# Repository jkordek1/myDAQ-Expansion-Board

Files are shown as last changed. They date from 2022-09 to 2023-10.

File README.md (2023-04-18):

# myDAQ Expansion Board


[]()



 Expansion board for NI myDAQ Student Data Acquisition Device, developed in 2022 for students studying at Zagreb university of applied sciences.
 It enables quick and easy .VI development without the need of connecting different modules via breadboard and jumpers.
 
 ## Features
 - Push buttons
 - Toggle switches
 - LEDs
 - BCD decoder for seven-segment display
 - L298n H-bridge used for powering two DC motors or one stepper motor
 - ACS712ELCTR-05B-T current sense IC for motor current measurement
 - External power supply for DC motors
 - Potentiometer
 - Light dependent resistor

## Images
<p align="center">
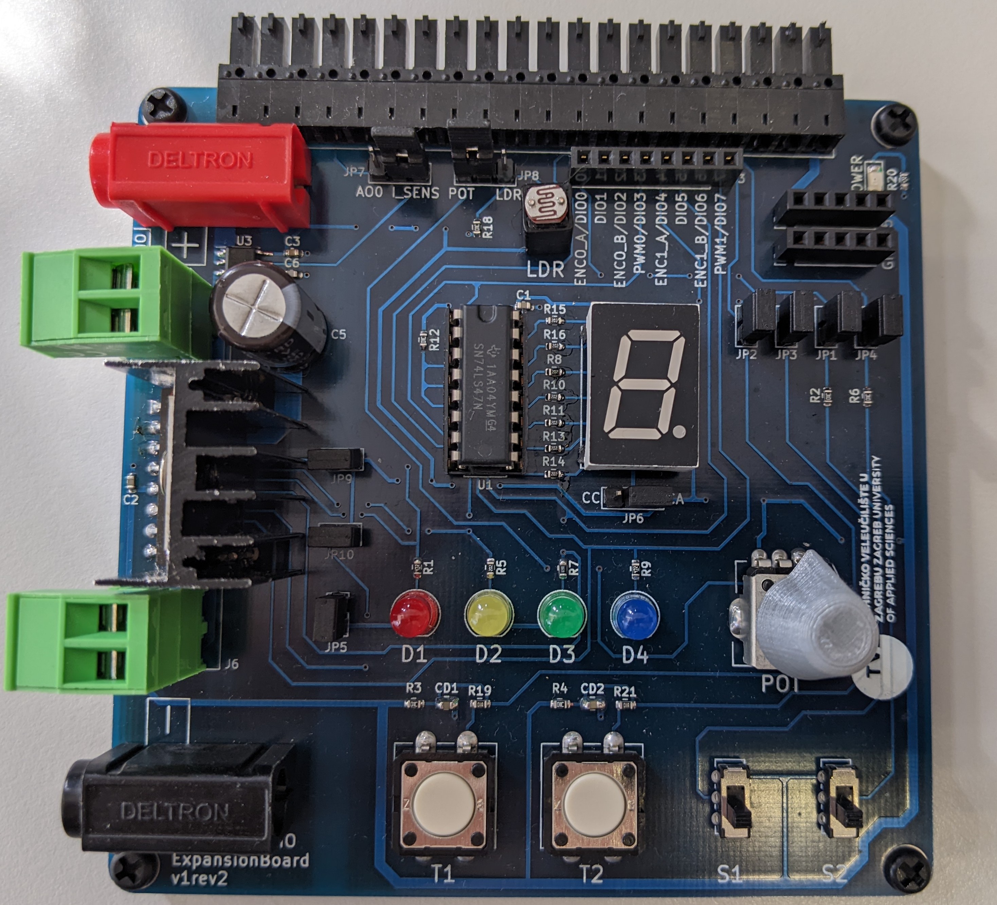
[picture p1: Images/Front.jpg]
  
</p>

## Project folder structure
    .
    ├── ...
    ├── 3DPrint                 # Files for 3D printing
    ├── Images                  # Images of the project
    ├── KiCADFiles              # Main folder
    │   ├── 3d models           # 3d models of components
    │   ├── Datasheet           # Datasheet collection
    │   ├── Graphics            # Custom graphics for PCB
    │   ├── gerber              # gerber output folder
    │   ├── myDAQExpansionBoard # Main folder for KiCAD files
    │   └── Schematic.pdf       # Project schematic
    └── ...

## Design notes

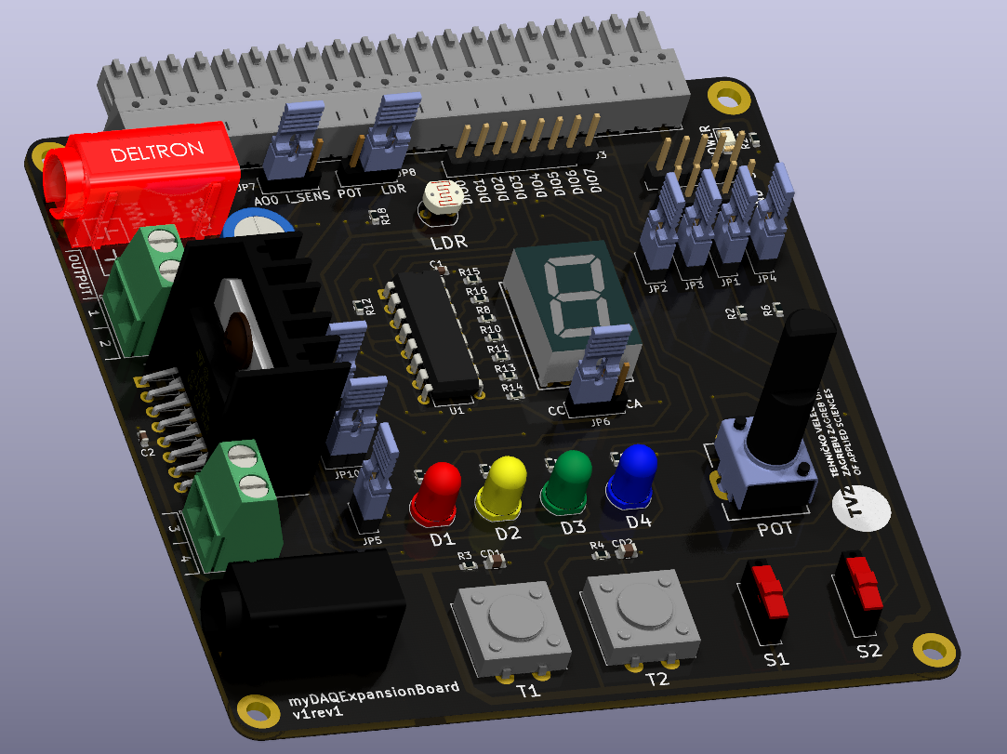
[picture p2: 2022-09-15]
Images/render_v1rev1.PNG

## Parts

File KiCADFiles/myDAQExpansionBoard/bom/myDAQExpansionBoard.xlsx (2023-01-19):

# | Naziv | Kućište | Količina | digikey/TME/mouser
1 | LED, crvena, 5mm THD | 5mm THD | 20
2 | LED, žuta, 5mm THD | 5mm THD | 20
3 | LED, zelena, 5mm THD | 5mm THD | 20
4 | LED, plava, 5mm THD | 5mm THD | 20
5 | LED, crvena, 1206 SMD | 1206 SMD | 20
6 | Otpornik 4k7, 0603 SMD | 0603 SMD | 40
7 | Otpornik 10k, 0603 SMD | 0603 SMD | 120
8 | Kondenzator 470uF, 35V | C_Radial_D10.0mm_H16.0mm_P5.00mm | 20 | 399-6657-1-ND (https://www.digikey.com/en/products/detail/kemet/ESK477M035AH2EA/3083072)
9 | Otpornik 2k, 0603 SMD | 0603 SMD | 160
10 | jumper, crni, 09200-71-BDGB00 | 09200-71-BDGB00 | 200 | 1849-09200-71-BDGB00-ND (https://www.digikey.com/en/products/detail/metz-connect-usa-inc/09200-71-bdgb00/13536314)
11 | jumper, crni, kraći, STC02SYAN | STC02SYAN | 200 | S9000-ND (https://www.digikey.com/en/products/detail/sullins-connector-solutions/STC02SYAN/76372?s=N4IgTCBcDaIMoE4AMKC0A5AIiAugXyA)
12 | Kondenzator 1uF, X7R, 50V, 0805 SMD | 0805 SMD | 40
13 | Kondenzator 1nF, X7R, 50V, 0603 SMD | 0603 SMD | 20
14 | Kondenzator 100nF, X7R, 50V, 0603 SMD | 0603 SMD | 80
15 | Potenciometar 10k, PTV09A-4225F-B103 | PTV09A-4225F-B103 | 20 | PTV09A-4225F-B103-ND (https://www.digikey.com/en/products/detail/bourns-inc/PTV09A-4225F-B103/3781155)
16 | Otpornik 619R, 0603 SMD | 0603 SMD | 20
17 | Otpornik 1k, 0603 SMD | 0603 SMD | 40
19 | 74LS47 | DIP-16_W7.62mm | 20 | TME (https://www.tme.eu/hr/details/74ls47/dekoderi-multiplekseri-prekidaci/texas-instruments/sn74ls47n/)
20 | Podnožje profi, DIP-16_W7.62mm | DIP-16_W7.62mm | 20
21 | ACS712ELCTR-05B | SOIC-8_3.9x4.9mm_P1.27mm | 20
22 | Buksna 4mm crvena PCB Deltron 571-0500 |  | 20 | 164-6219 (https://hr.mouser.com/ProductDetail/Deltron/571-0500?qs=E2gf03EXmtqN5S6PKlh9vA%3D%3D)
23 | Buksna 4mm cna PCB Deltron 571-0100 |  | 20 | 164-6218 (https://hr.mouser.com/ProductDetail/Deltron/571-0100?qs=E2gf03EXmtoqC8%2FBhoPdrg%3D%3D)
24 | Otpornik 6k8 | 0603 SMD | 20
26 | B3F-4000 |  | 40 | SW411-ND (https://www.digikey.com/en/products/detail/omron-electronics-inc-emc-div/b3f-4000/63961)
27 | Letvica, M, 2.54mm pitch, 1x20 |  | 20
28 | Letvica, Ž, 2.54mm pitch, 1x8 |  | 20
29 | Letvica, Ž, 2.54mm pitch, 1x5 |  | 20
30 | 7 segm displej, crveni, CA | 17.5x12.6mm, Terminal pitch 2.54mm, Row pitch 15.24mm | 20
31 | Ispitni kabelić, crveni, 0.8-1.0m, 5A |  | 20
32 | Ispitni kabelić, crni, 0.8-1.0m, 5A |  | 20
39 | plastična m3 matica |  |  |  | kupljeno
35 | hladnjak |  | 1
36 | Plastični odstojnik M3, duljina 5mm |  | 4
40 | gumene nožice
41 | m3 vijci i matice
42 | vijci bez glave za spojnicu
43 | enkoderi 360 impulsa
44 | navoji za 3d print

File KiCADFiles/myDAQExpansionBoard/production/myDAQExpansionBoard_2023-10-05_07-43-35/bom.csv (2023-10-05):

Designator | Footprint | Quantity | Value | LCSC Part #
C1, C2, C3, C4 | 0603 | 4 | 100n
C5 | C_Radial_D10.0mm_H16.0mm_P5.00mm | 1 | 470u
C6 | 0603 | 1 | 1n
CD1, CD2 | 0805 | 2 | 100n
D1 | LED_D5.0mm | 1 | RED
D10, D11, D12, D5, D6, D7, D8, D9 | D_SMA | 8 | 1N4007
D14 | 1206 | 1 | LED
D2 | LED_D5.0mm | 1 | YELLOW
D3 | LED_D5.0mm | 1 | GREEN
D4 | LED_D5.0mm | 1 | BLUE
H1, H2, H3, H4 | MountingHole_3.2mm_M3_ISO7380_Pad | 4 | MountingHole_Pad
J1, J2 | PinHeader_1x05_P2.54mm_Vertical | 2 | Conn_01x05_Male
J3 | PinHeader_1x08_P2.54mm_Vertical | 1 | Conn_01x08_Male
J4 | OSTV7XX3151 | 1 | OSTV7XX3151
J5, J6 | TerminalBlock_Phoenix_MKDS-1,5-2-5.08_1x02_P5.08mm_Horizontal | 2 | Screw_Terminal_01x02
J7 | DELTRON 4mm banana socket - red | 1 | Screw_Terminal_01x01
J8 | DELTRON 4mm banana socket - black | 1 | Screw_Terminal_01x01
JP1, JP10, JP2, JP3, JP4, JP5, JP9 | PinHeader_1x02_P2.54mm_jumper | 7 | Jumper_2_Open
JP6, JP7, JP8 | PinHeader_1x03_P2.54mm_Vertical_jumper | 3 | Jumper_3_Open
R1, R20, R9 | 0603 | 3 | 4k7
R10, R11, R13, R14, R15, R16, R5, R8 | 0603 | 8 | 2k
R12, R18, R2, R3, R4, R6 | 0603 | 6 | 10k
R17 | R_LDR_5.1x4.3mm_P3.4mm_Vertical | 1 | R_Photo
R19, R21 | 0603 | 2 | 100
R7 | 0603 | 1 | 619
RV1 | PTV09A-4225F-B502 | 1 | 10k
SW1, SW2 | EG1271A | 2 | SW_SPDT
SW3, SW4 | Omron_B3F-12x12mm | 2 | SW_Push
U1 | DIP-16_W7.62mm | 1 | 74LS47
U2 | 7segm-SA52 | 1 | 7segm-symbol
U3 | SOIC-8_3.9x4.9mm_P1.27mm | 1 | ACS712xLCTR-05B
U4 | L298n | 1 | L298N

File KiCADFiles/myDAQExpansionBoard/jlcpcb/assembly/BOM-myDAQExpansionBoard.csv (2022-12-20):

Comment | Designator | Footprint | LCSC
2k | R11 | R_0603_1608Metric
MountingHole_Pad | H1 | MountingHole_3.2mm_M3_ISO7380_Pad
BLUE | D4 | LED_D5.0mm
SW_SPDT | SW1 | 500SSP1S1M2QEA
1u | CD2 | C_0805_2012Metric
Jumper_2_Open | JP5 | PinHeader_1x02_P2.54mm_jumper
100n | C3 | C_0603_1608Metric
SW_Push | SW4 | Omron_B3F-12x12mm
Jumper_2_Open | JP10 | PinHeader_1x02_P2.54mm_jumper
10k | R3 | R_0603_1608Metric
Jumper_2_Open | JP1 | PinHeader_1x02_P2.54mm_jumper
Conn_01x05_Male | J2 | PinHeader_1x05_P2.54mm_Vertical
SW_SPDT | SW2 | 500SSP1S1M2QEA
Screw_Terminal_01x02 | J6 | TerminalBlock_Phoenix_MKDS-1,5-2-5.08_1x02_P5.08mm_Horizontal
100n | C4 | C_0603_1608Metric
YELLOW | D2 | LED_D5.0mm
2k | R13 | R_0603_1608Metric
2k | R8 | R_0603_1608Metric
MountingHole_Pad | H4 | MountingHole_3.2mm_M3_ISO7380_Pad
SW_Push | SW3 | Omron_B3F-12x12mm
Jumper_2_Open | JP2 | PinHeader_1x02_P2.54mm_jumper
Conn_01x05_Male | J1 | PinHeader_1x05_P2.54mm_Vertical
ACS712xLCTR-05B | U3 | SOIC-8_3.9x4.9mm_P1.27mm
Jumper_2_Open | JP9 | PinHeader_1x02_P2.54mm_jumper
74LS47 | U1 | DIP-16_W7.62mm
10k | R18 | R_0603_1608Metric
Jumper_2_Open | JP3 | PinHeader_1x02_P2.54mm_jumper
4k7 | R20 | R_0603_1608Metric
1u | CD1 | C_0805_2012Metric
4k7 | R1 | R_0603_1608Metric
100n | C1 | C_0603_1608Metric
7segm-symbol | U2 | 7segm-SA52
MountingHole_Pad | H2 | MountingHole_3.2mm_M3_ISO7380_Pad
10k | R4 | R_0603_1608Metric
100n | C2 | C_0603_1608Metric
L298N | U4 | L298n
RED | D1 | LED_D5.0mm
MountingHole_Pad | H3 | MountingHole_3.2mm_M3_ISO7380_Pad
Screw_Terminal_01x01 | J8 | DELTRON 4mm banana socket - black
2k | R14 | R_0603_1608Metric
Jumper_2_Open | JP4 | PinHeader_1x02_P2.54mm_jumper
R_Photo | R17 | R_LDR_5.1x4.3mm_P3.4mm_Vertical
2k | R15 | R_0603_1608Metric
10k | R12 | R_0603_1608Metric
2k | R10 | R_0603_1608Metric
10k | R6 | R_0603_1608Metric
2k | R16 | R_0603_1608Metric
GREEN | D3 | LED_D5.0mm
2k | R5 | R_0603_1608Metric
1k | R19 | R_0603_1608Metric
Screw_Terminal_01x02 | J5 | TerminalBlock_Phoenix_MKDS-1,5-2-5.08_1x02_P5.08mm_Horizontal
Conn_01x08_Male | J3 | PinHeader_1x08_P2.54mm_Vertical
Screw_Terminal_01x01 | J7 | DELTRON 4mm banana socket - red
6k8 | R9 | R_0603_1608Metric
619 | R7 | R_0603_1608Metric
10k | R2 | R_0603_1608Metric
OSTV7XX3151 | J4 | OSTV7XX3151
470u | C5 | C_Radial_D10.0mm_H16.0mm_P5.00mm
Jumper_3_Open | JP8 | PinHeader_1x03_P2.54mm_Vertical_jumper
10k | RV1 | PTV09A-4225F-B502
Jumper_3_Open | JP7 | PinHeader_1x03_P2.54mm_Vertical_jumper
1n | C6 | C_0603_1608Metric
Jumper_3_Open | JP6 | PinHeader_1x03_P2.54mm_Vertical_jumper
LED | D14 | LED_1206_3216Metric
1N4007 | D6 | D_SMA
1N4007 | D5 | D_SMA
1N4007 | D10 | D_SMA
1N4007 | D11 | D_SMA
1N4007 | D9 | D_SMA
1N4007 | D7 | D_SMA
1N4007 | D12 | D_SMA
1N4007 | D8 | D_SMA
1k | R21 | R_0603_1608Metric

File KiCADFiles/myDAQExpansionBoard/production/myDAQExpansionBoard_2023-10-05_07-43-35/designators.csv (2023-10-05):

C1:1
C2:1
C3:1
C4:1
C5:1
C6:1
CD1:1
CD2:1
D1:1
D10:1
D11:1
D12:1
D14:1
D2:1
D3:1
D4:1
D5:1
D6:1
D7:1
D8:1
D9:1
G***:2
H1:1
H2:1
H3:1
H4:1
J1:1
J2:1
J3:1
J4:1
J5:1
J6:1
J7:1
J8:1
JP1:1
JP10:1
JP2:1
JP3:1
JP4:1
JP5:1
JP6:1
JP7:1
JP8:1
JP9:1
R1:1
R10:1
R11:1
R12:1
R13:1
R14:1
R15:1
R16:1
R17:1
R18:1
R19:1
R2:1
R20:1
R21:1
R3:1
R4:1
R5:1
R6:1
R7:1
R8:1
R9:1
RV1:1
SW1:1
SW2:1
SW3:1
SW4:1
U1:1
U2:1
U3:1
U4:1

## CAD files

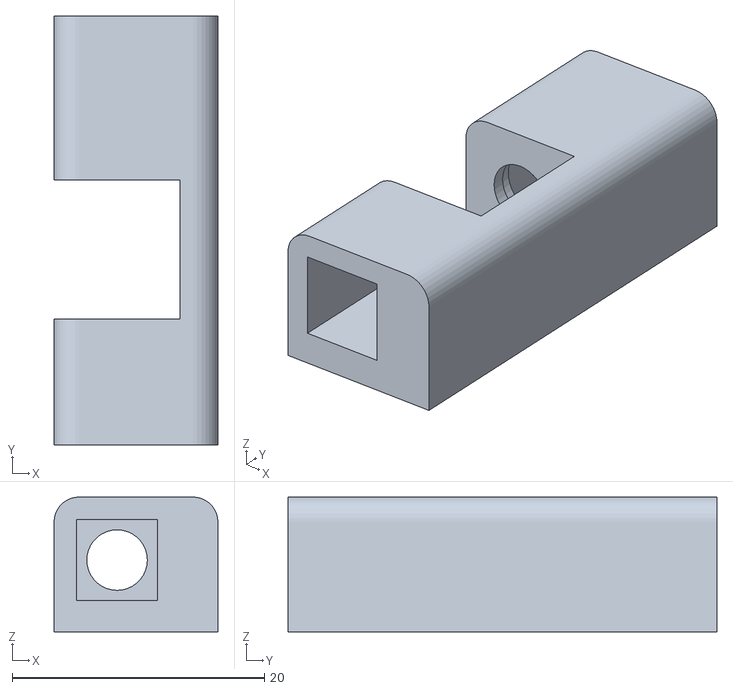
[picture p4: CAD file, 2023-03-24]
3DPrint/Drzac ledice.STL
13.0 x 34.0 x 10.7

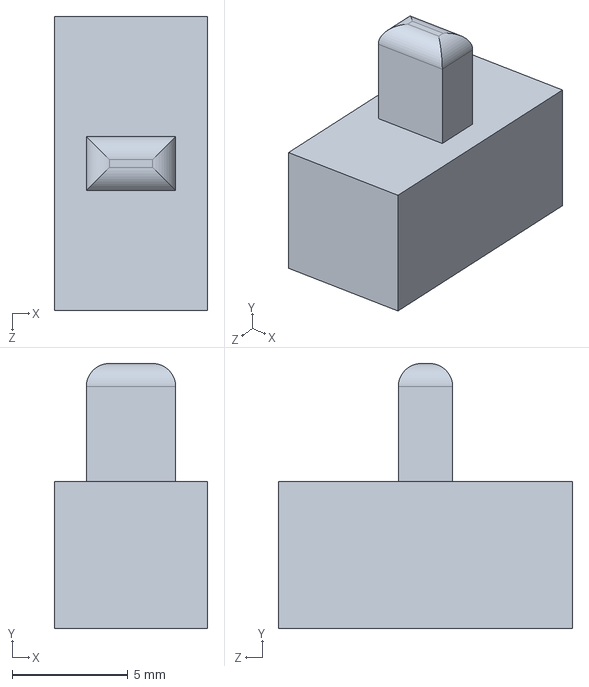
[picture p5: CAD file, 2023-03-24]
KiCADFiles/3d models/Part1.SLDPRT
6.60 x 11.4 x 12.7 mm

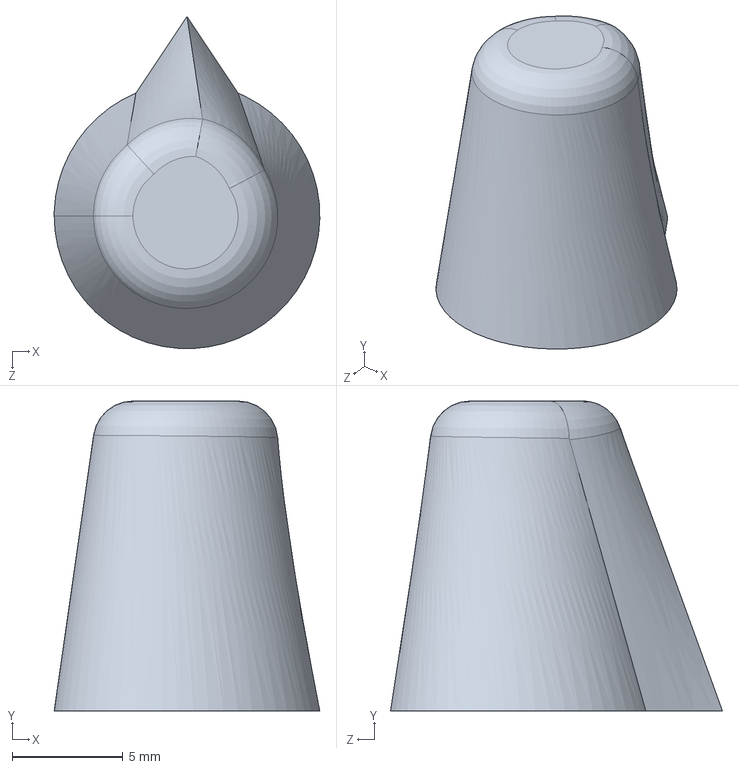
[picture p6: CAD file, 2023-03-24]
3DPrint/knob.SLDPRT
12.0 x 14.0 x 15.0 mm

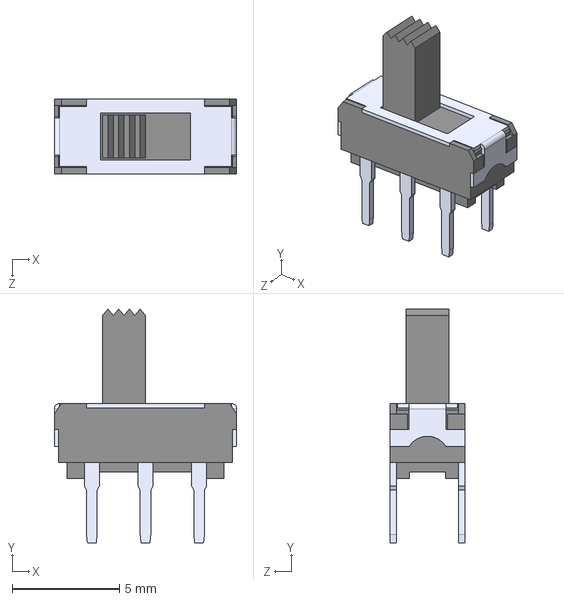
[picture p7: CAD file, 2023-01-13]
KiCADFiles/3d models/EG1271A.STEP
8.50 x 10.9 x 3.50 mm

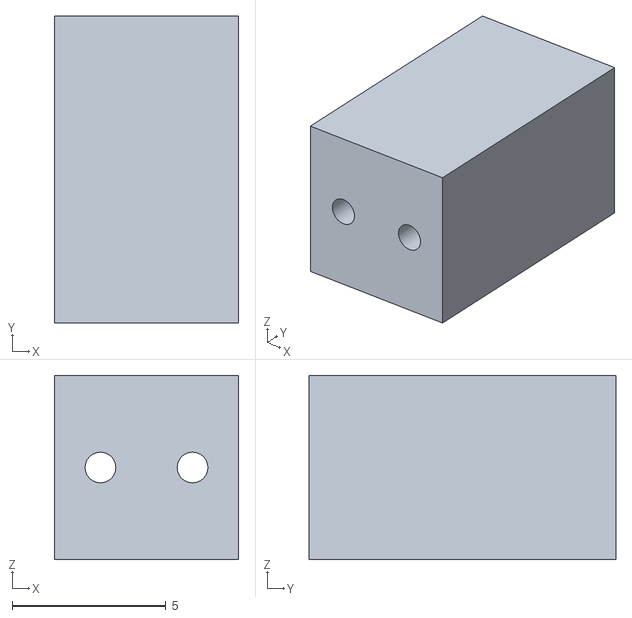
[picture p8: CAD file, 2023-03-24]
3DPrint/Odstojnik za ldr.STL
6.00 x 10.0 x 6.00

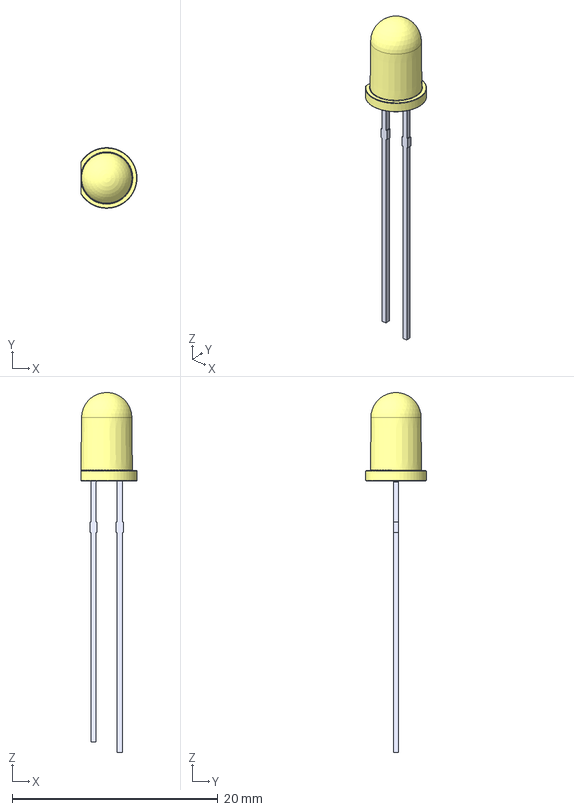
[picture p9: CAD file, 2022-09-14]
KiCADFiles/3d models/LED D5 - Yellow.step
5.45 x 5.90 x 35.0 mm

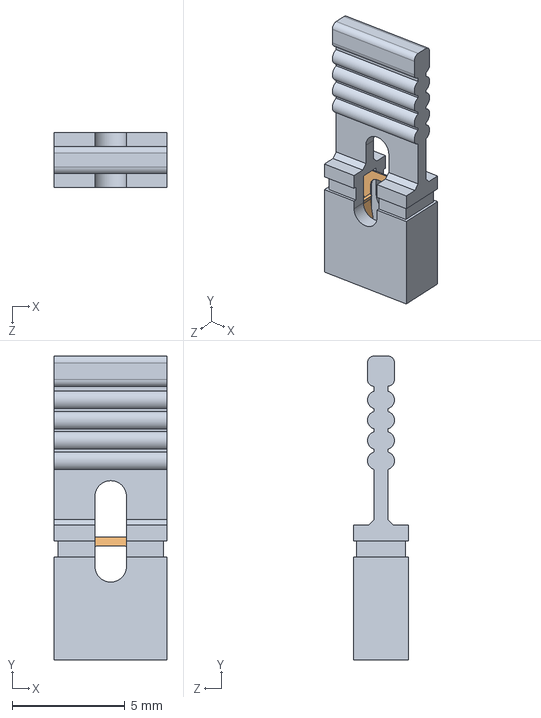
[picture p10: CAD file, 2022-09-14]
KiCADFiles/3d models/_ _C02SXON-RC.STEP
5.00 x 13.5 x 2.44 mm

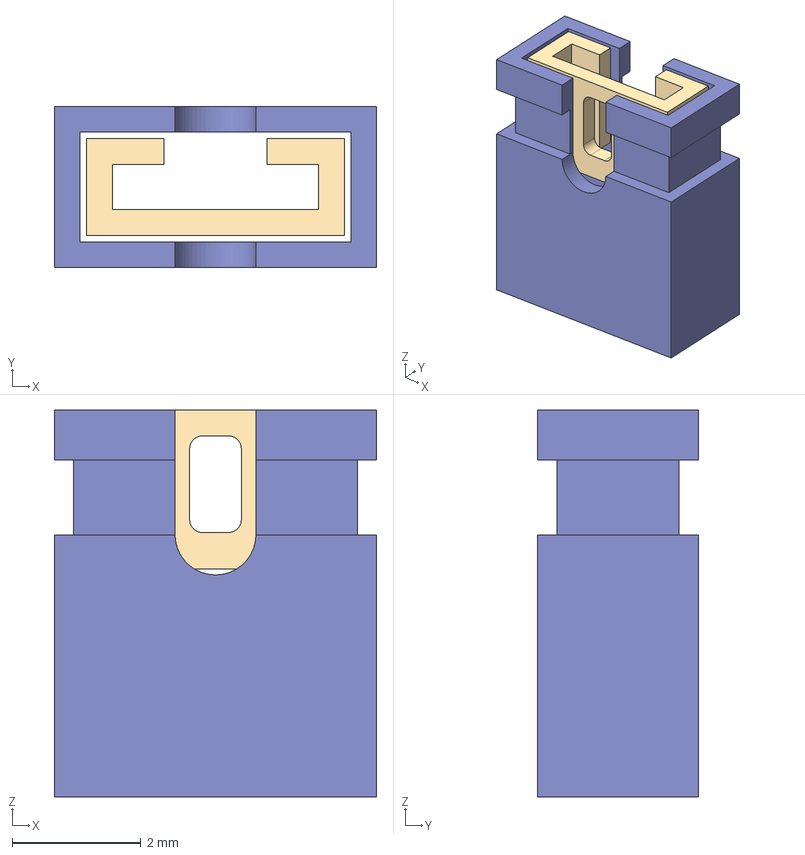
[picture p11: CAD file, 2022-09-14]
KiCADFiles/3d models/Pin header jumper.stp
5.00 x 2.50 x 6.00 mm

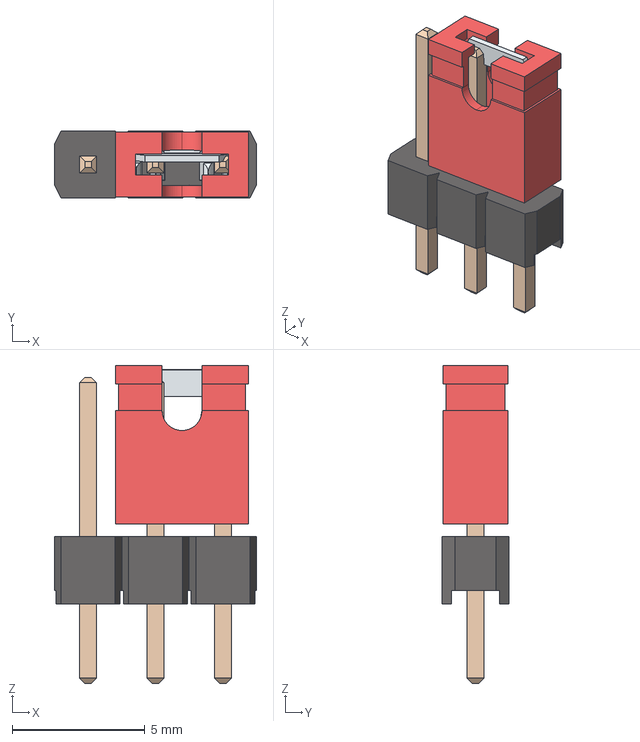
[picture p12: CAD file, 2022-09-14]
KiCADFiles/3d models/pin header 1x3 and jumper.stp
7.62 x 2.54 x 12.0 mm

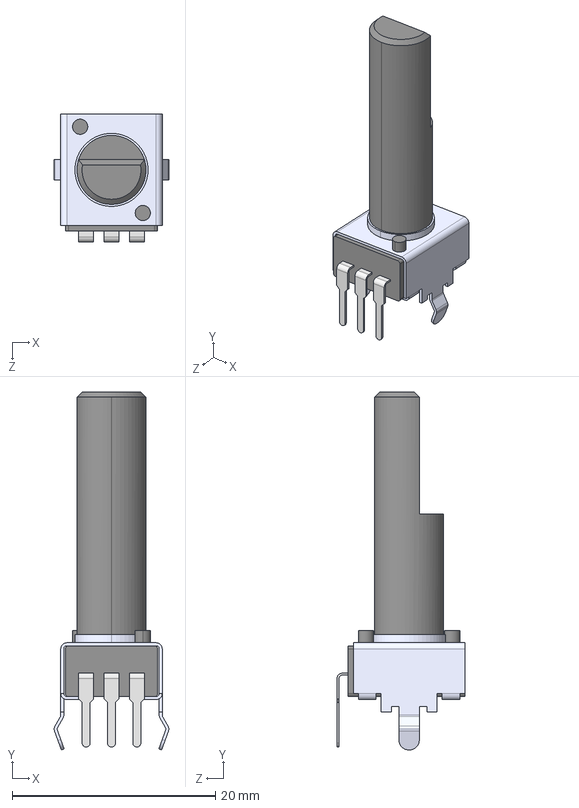
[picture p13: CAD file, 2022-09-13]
KiCADFiles/3d models/PTV09A-4.STEP
11.3 x 35.3 x 12.6 mm
櫻蠉錪1
櫻蠉錪2
櫻蠉錪3

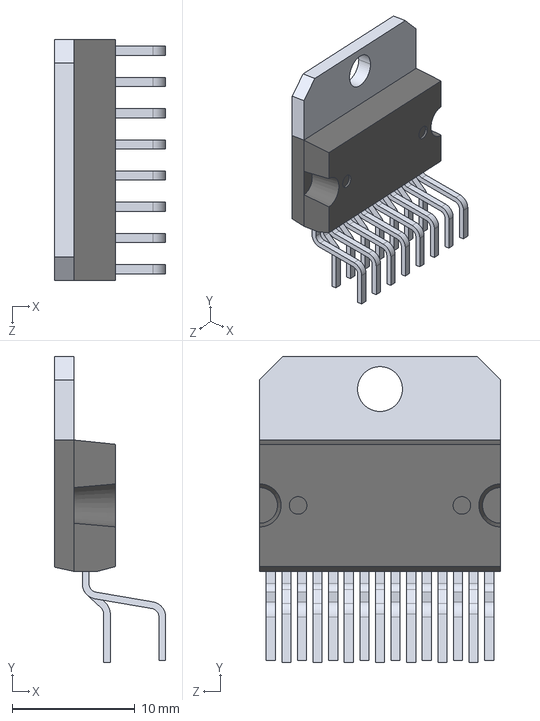
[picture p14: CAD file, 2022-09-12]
KiCADFiles/3d models/MULTIWAT T15.step
9.07 x 24.9 x 19.6 mm

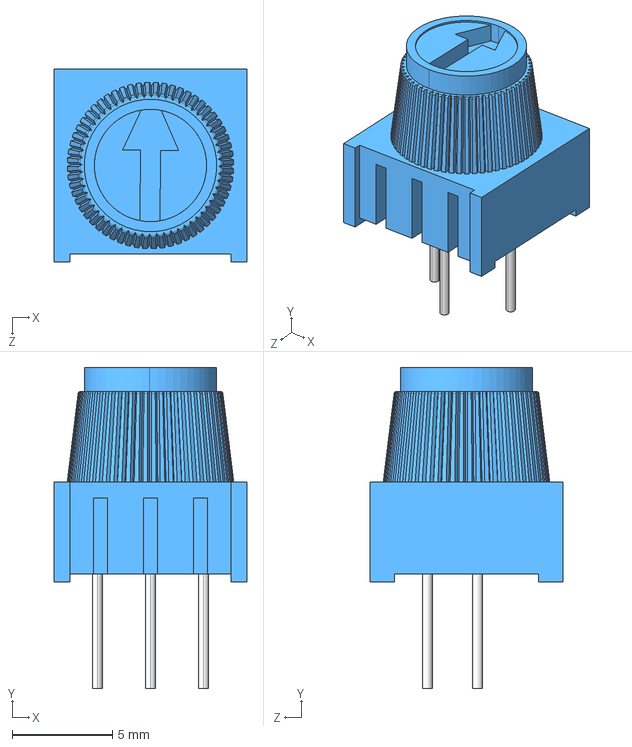
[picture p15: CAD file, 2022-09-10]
KiCADFiles/3d models/10 KILO-OHM BREADBOARD TRIM POTENTIOMETER WITH KNOB.STEP
9.60 x 16.0 x 9.60 mm
BASE, 10 KILO-OHM BREADBOARD TRIM POTENTIOMETER WITH KNOB
KNOB, 10 KILO-OHM BREADBOARD TRIM POTENTIOMETER WITH KNOB

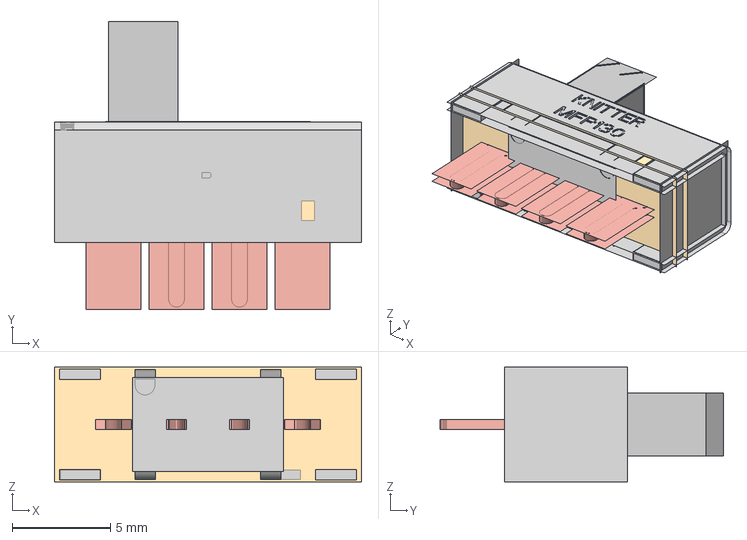
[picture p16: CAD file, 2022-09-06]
KiCADFiles/3d models/MFP 130.igs
15.6 x 14.6 x 5.82 mm

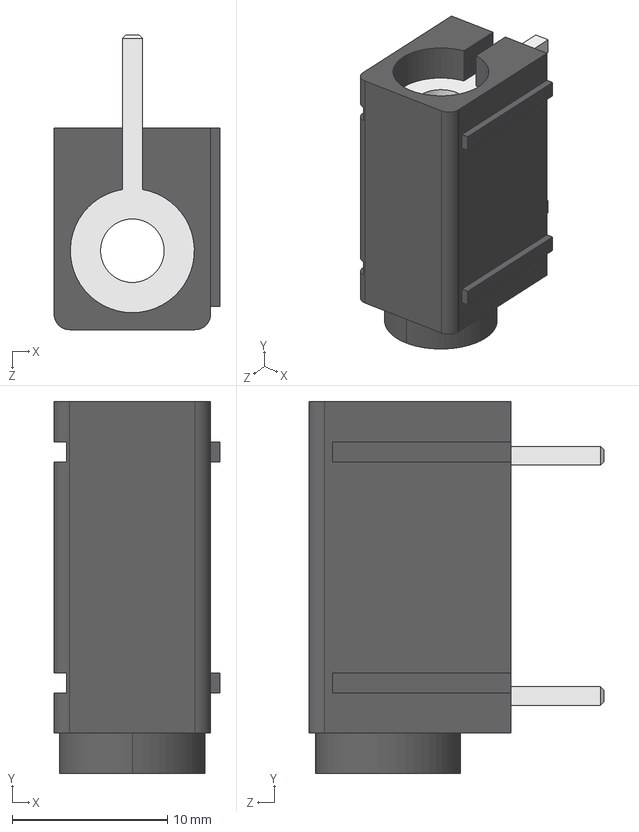
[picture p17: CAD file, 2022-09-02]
KiCADFiles/3d models/AB2_90DEG_4MM_JACK_PTH-BLK.STEP
10.7 x 24.0 x 19.0 mm

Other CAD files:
KiCADFiles/3d models/500SSP1S1M2QEA.STEP
KiCADFiles/3d models/LED D5 - Blue.step
KiCADFiles/3d models/LED D5 - Green.step
KiCADFiles/3d models/LED D5 - Red.step
KiCADFiles/3d models/B3F_4005.step
KiCADFiles/3d models/DIP-16 on SCSM-16.step
KiCADFiles/3d models/MFP_130_1682673224.214.step
KiCADFiles/3d models/OSTV7203151.stp
KiCADFiles/3d models/SX52.STEP

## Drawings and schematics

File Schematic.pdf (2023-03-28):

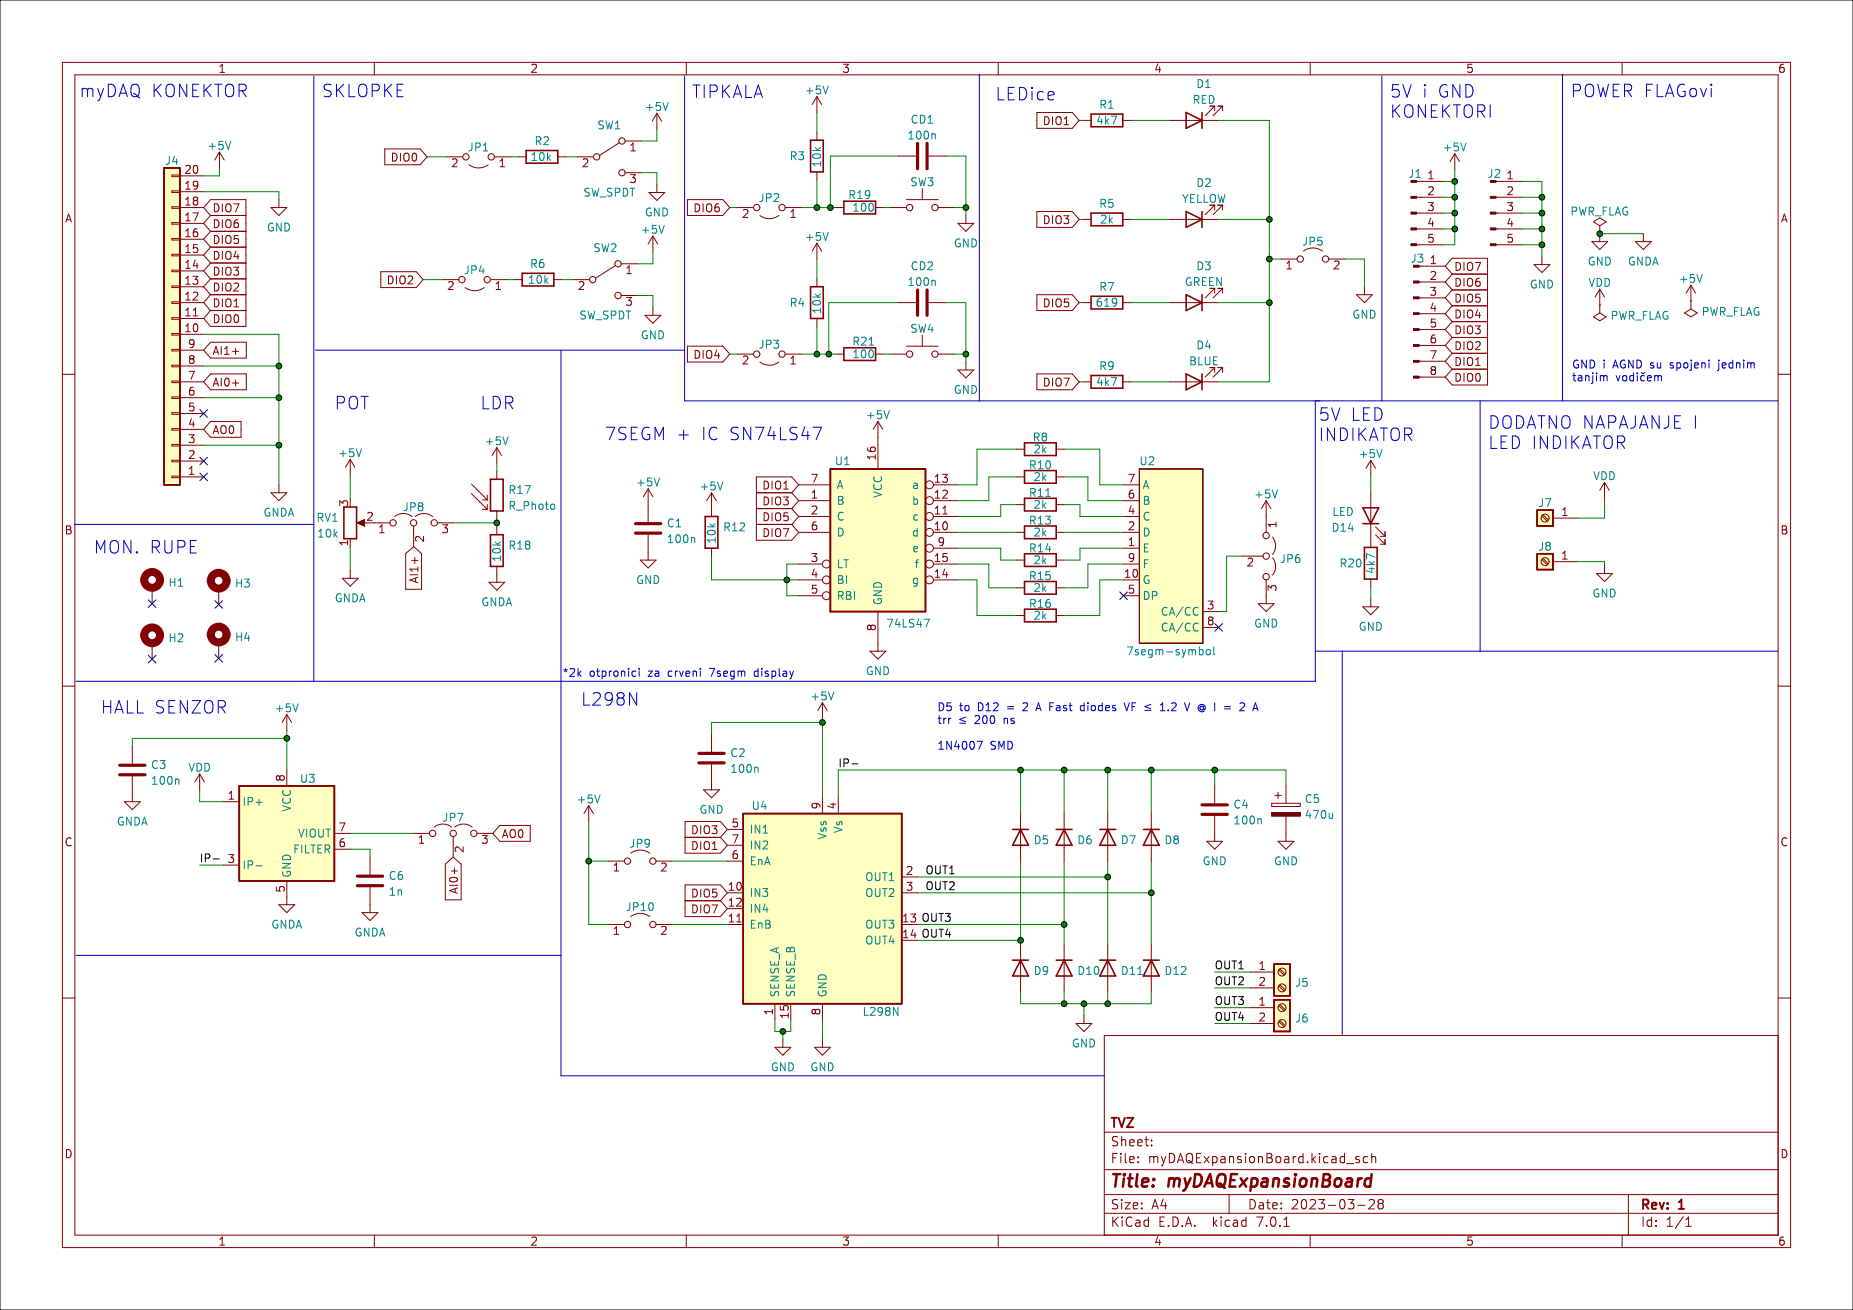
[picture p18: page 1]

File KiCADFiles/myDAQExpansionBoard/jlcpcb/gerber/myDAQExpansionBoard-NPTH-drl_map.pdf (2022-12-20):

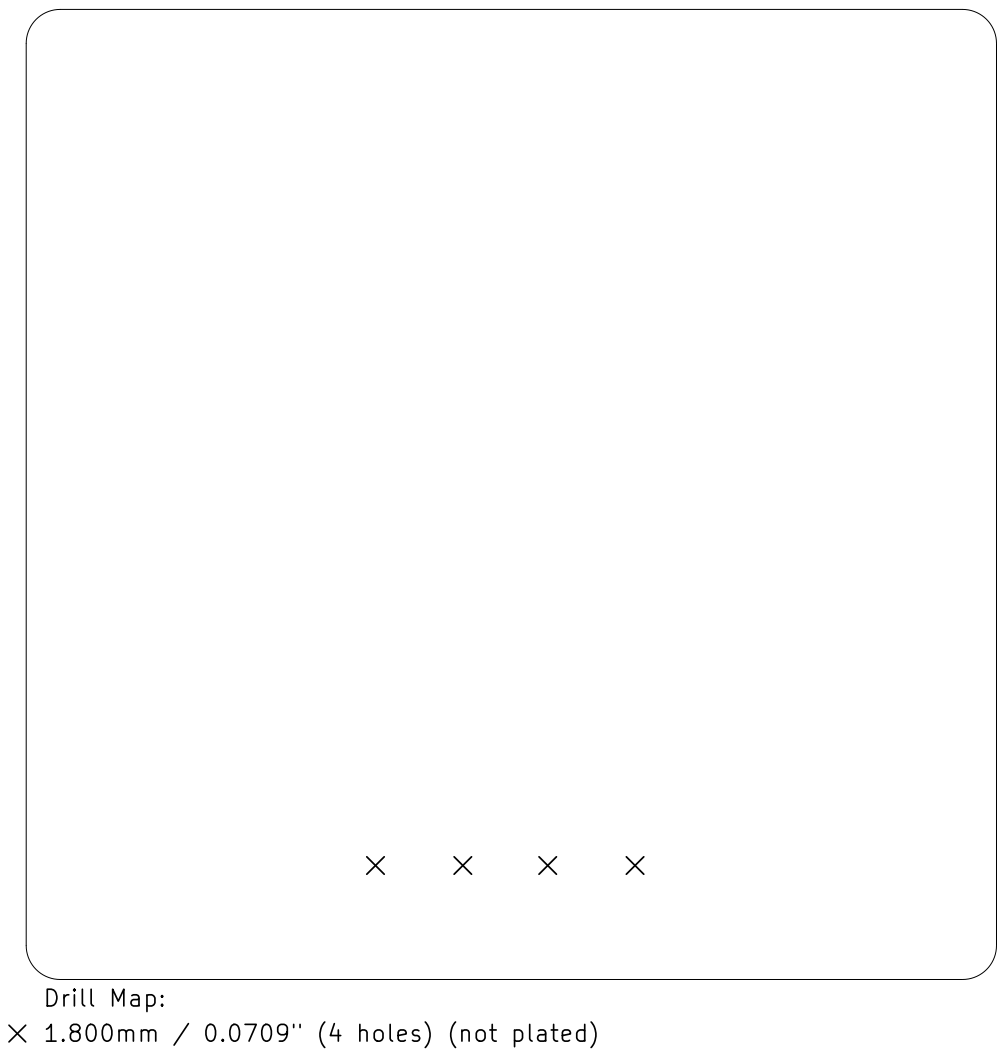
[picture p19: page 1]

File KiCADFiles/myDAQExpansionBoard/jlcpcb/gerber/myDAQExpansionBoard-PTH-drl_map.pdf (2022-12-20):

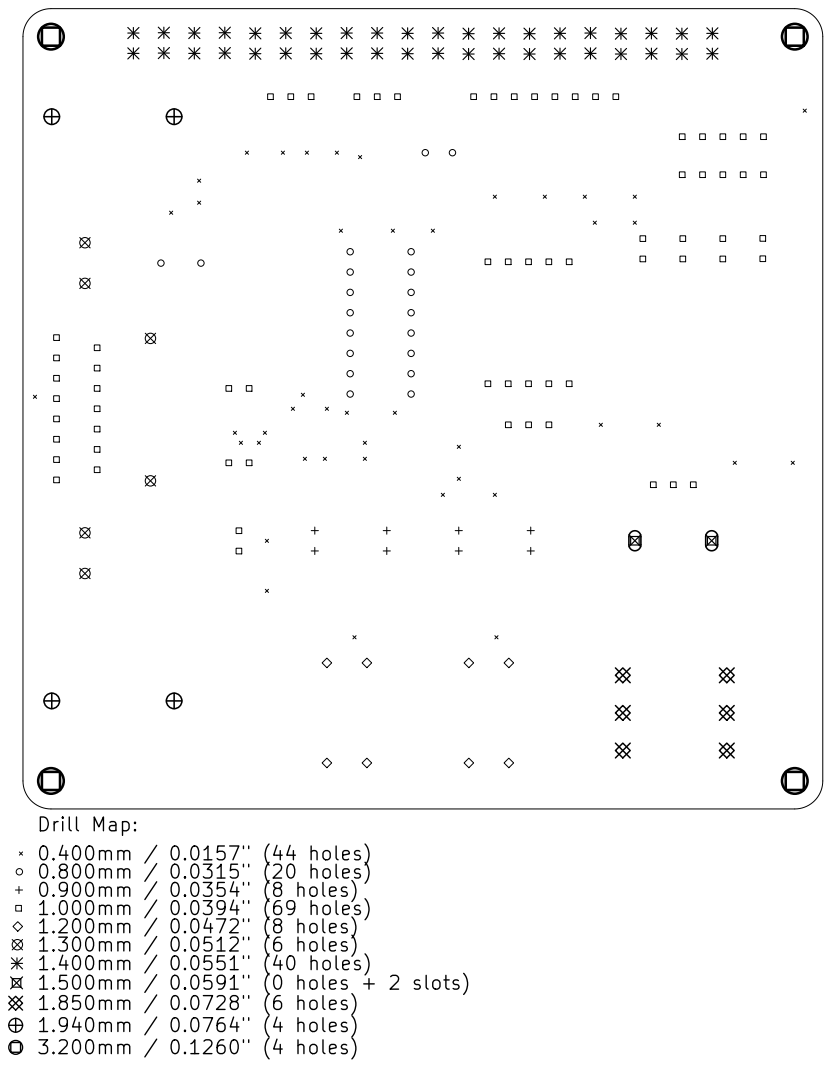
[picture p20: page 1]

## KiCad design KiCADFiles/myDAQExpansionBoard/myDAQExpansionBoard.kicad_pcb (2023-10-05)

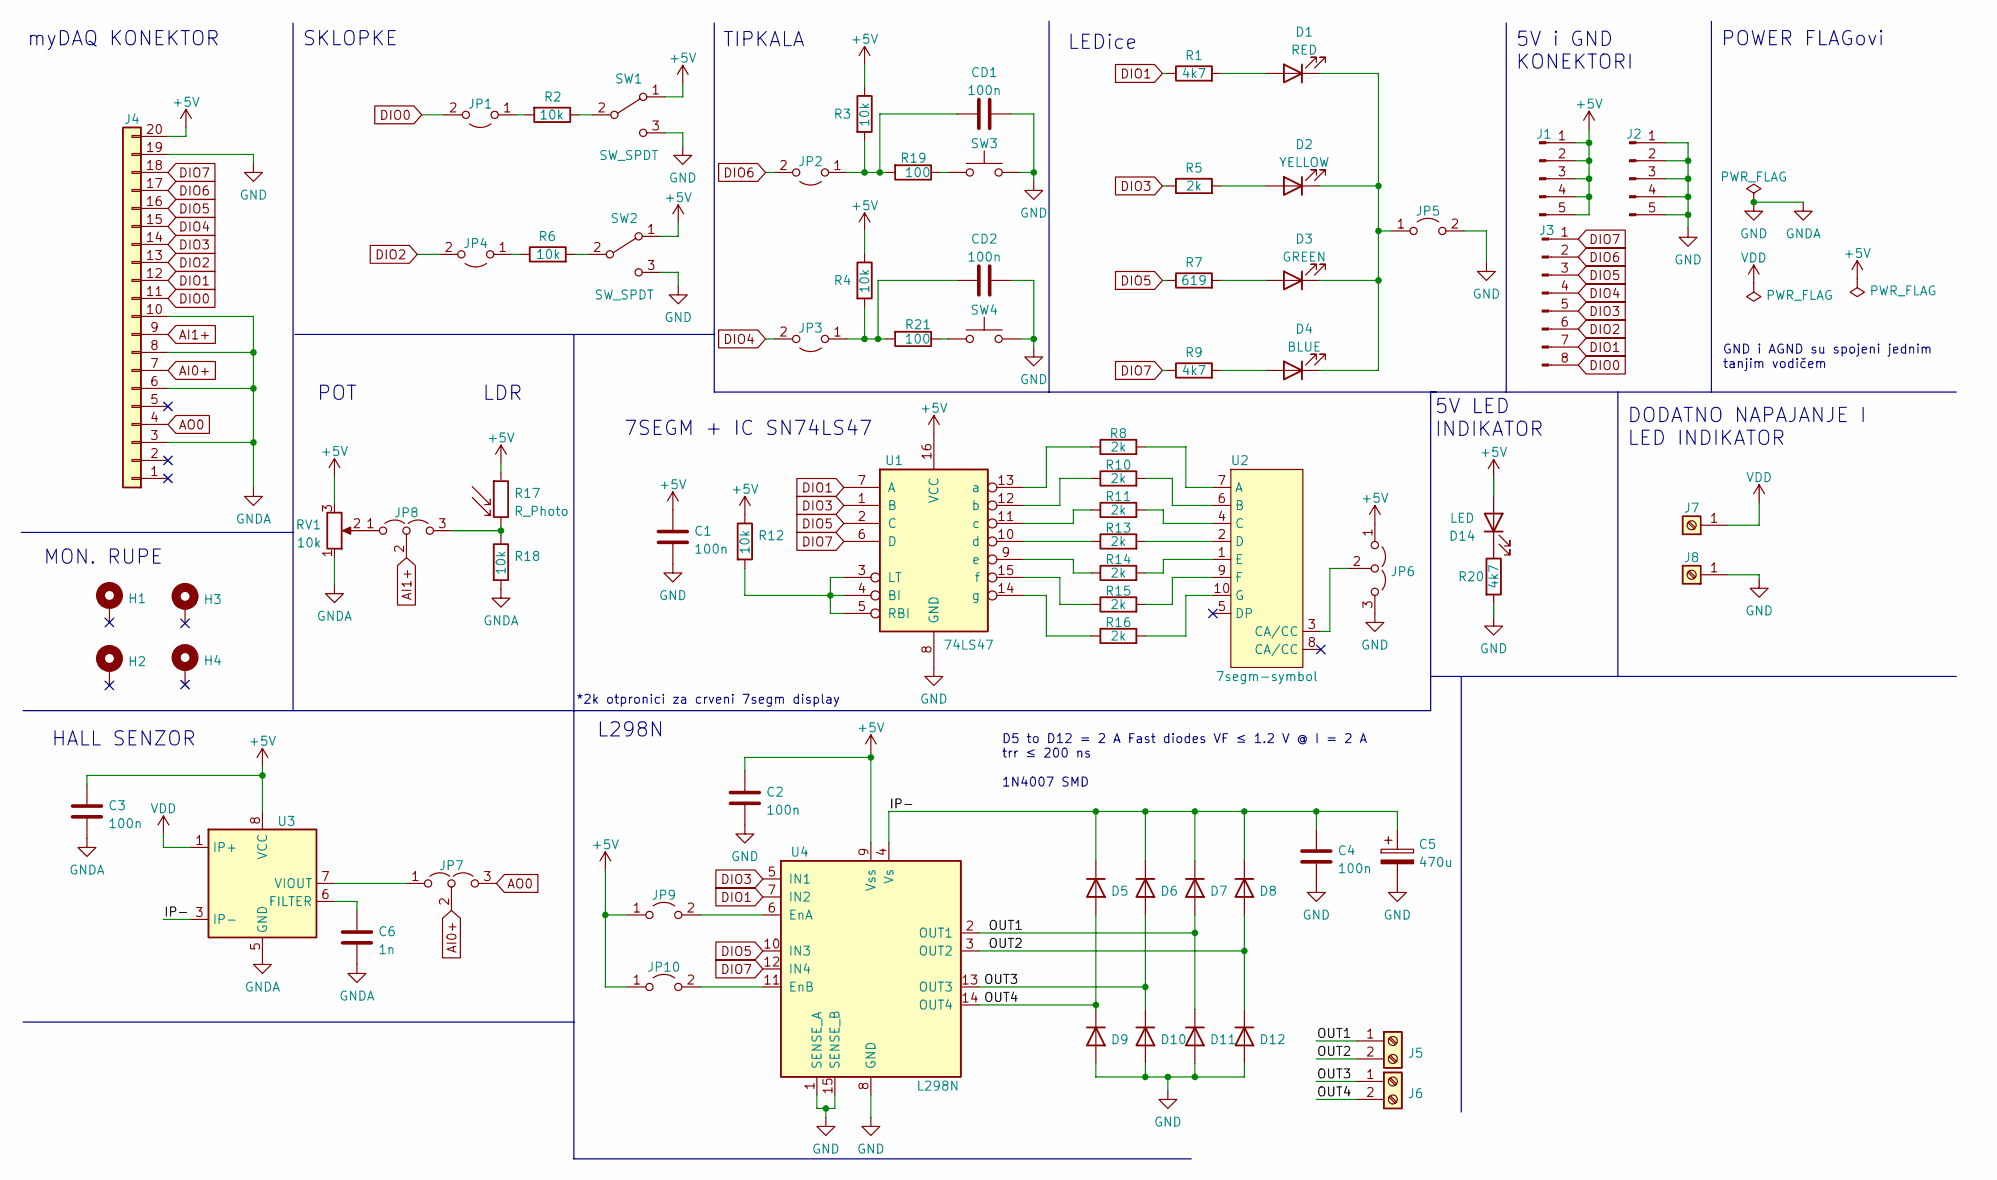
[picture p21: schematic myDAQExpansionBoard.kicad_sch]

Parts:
C1, C2, C3, C4: 100n; C_0603_1608Metric
C5: 470u; C_Radial_D10.0mm_H16.0mm_P5.00mm
C6: 1n; C_0603_1608Metric
CD1, CD2: 100n; C_0805_2012Metric
D1: RED; LED_D5.0mm
D2: YELLOW; LED_D5.0mm
D3: GREEN; LED_D5.0mm
D4: BLUE; LED_D5.0mm
D5, D6, D7, D8, D9, D10, D11, D12: 1N4007; D_SMA
D14: LED; LED_1206_3216Metric
H1, H2, H3, H4: MountingHole_Pad; MountingHole_3.2mm_M3_ISO7380_Pad
J1, J2: Conn_01x05_Male; PinHeader_1x05_P2.54mm_Vertical
J3: Conn_01x08_Male; PinHeader_1x08_P2.54mm_Vertical
J4: OSTV7XX3151
J5, J6: Screw_Terminal_01x02; TerminalBlock_Phoenix_MKDS-1,5-2-5.08_1x02_P5.08mm_Horizont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
J7: Screw_Terminal_01x01; DELTRON 4mm banana socket - red
J8: Screw_Terminal_01x01; DELTRON 4mm banana socket - black
JP1, JP2, JP3, JP4, JP5, JP9, JP10: Jumper_2_Open; PinHeader_1x02_P2.54mm_jumper
JP6, JP7, JP8: Jumper_3_Open; PinHeader_1x03_P2.54mm_Vertical_jumper
R1, R9, R20: 4k7; R_0603_1608Metric
R2, R3, R4, R6, R12, R18: 10k; R_0603_1608Metric
R5, R8, R10, R11, R13, R14, R15, R16: 2k; R_0603_1608Metric
R7: 619; R_0603_1608Metric
R17: R_Photo; R_LDR_5.1x4.3mm_P3.4mm_Vertical
R19, R21: 100; R_0603_1608Metric
RV1: 10k; PTV09A-4225F-B502
SW1, SW2: SW_SPDT; EG1271A
SW3, SW4: SW_Push; Omron_B3F-12x12mm
U1: 74LS47; DIP-16_W7.62mm
U2: 7segm-symbol; 7segm-SA52
U3: ACS712xLCTR-05B; SOIC-8_3.9x4.9mm_P1.27mm
U4: L298N; L298n

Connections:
+5V: C1.1, C2.1, C3.1, D14.2 (A), J1.1, J1.2, J1.3, J1.4, J1.5, J4.20, JP6.1 (A), JP9.1 (A), JP10.1 (A), R3.1, R4.1, R12.1, R17.1, RV1.3, SW1.1 (A), SW2.1 (A), U1.16 (VCC), U3.8 (VCC), U4.9 (Vss)
/IP-: C4.1, C5.1, D5.1 (K), D6.1 (K), D7.1 (K), D8.1 (K), U3.3 (IP-), U3.4 (IP-), U4.4 (Vs)
/OUT1: D7.2 (A), D11.1 (K), J5.1, U4.2 (OUT1)
/OUT2: D8.2 (A), D12.1 (K), J5.2, U4.3 (OUT2)
/OUT3: D6.2 (A), D10.1 (K), J6.1, U4.13 (OUT3)
/OUT4: D5.2 (A), D9.1 (K), J6.2, U4.14 (OUT4)
AI0+: J4.7, JP7.2 (C)
AI1+: J4.9, JP8.2 (C)
AO0: J4.4, JP7.3 (B)
DIO0: J3.8, J4.11, JP1.2 (B)
DIO1: J3.7, J4.12, R1.1, U1.7 (A), U4.7 (IN2)
DIO2: J3.6, J4.13, JP4.2 (B)
DIO3: J3.5, J4.14, R5.1, U1.1 (B), U4.5 (IN1)
DIO4: J3.4, J4.15, JP3.2 (B)
DIO5: J3.3, J4.16, R7.1, U1.2 (C), U4.10 (IN3)
DIO6: J3.2, J4.17, JP2.2 (B)
DIO7: J3.1, J4.18, R9.1, U1.6 (D), U4.12 (IN4)
GND: C1.2, C2.2, C3.2, C4.2, C5.2, C6.2, CD1.2, CD2.2, D9.2 (A), D10.2 (A), D11.2 (A), D12.2 (A), J2.1, J2.2, J2.3, J2.4, J2.5, J4.3, J4.6, J4.8, J4.10, J4.19, J8.1, JP5.2 (B), JP6.3 (B), R18.2, R20.2, RV1.1, SW1.3 (C), SW2.3 (C), SW3.2, SW4.2, U1.8 (GND), U3.5 (GND), U4.1 (SENSE_A), U4.8 (GND), U4.15 (SENSE_B)
unnamed: C6.1, U3.6 (FILTER)
unnamed: CD1.1, JP2.1 (A), R3.2, R19.2
unnamed: CD2.1, JP3.1 (A), R4.2, R21.2
unnamed: D1.1 (K), D2.1 (K), D3.1 (K), D4.1 (K), JP5.1 (A)
unnamed: D1.2 (A), R1.2
unnamed: D2.2 (A), R5.2
unnamed: D3.2 (A), R7.2
unnamed: D4.2 (A), R9.2
unnamed: D14.1 (K), R20.1
unnamed: JP1.1 (A), R2.2
unnamed: JP4.1 (A), R6.1
unnamed: JP6.2 (C), U2.3 (CA/CC)
unnamed: JP7.1 (A), U3.7 (VIOUT)
unnamed: JP8.1 (A), RV1.2
unnamed: JP8.3 (B), R17.2, R18.1
unnamed: JP9.2 (B), U4.6 (EnA)
unnamed: JP10.2 (B), U4.11 (EnB)
unnamed: R2.1, SW1.2 (B)
unnamed: R6.2, SW2.2 (B)
unnamed: R8.1, U1.13 (a)
unnamed: R8.2, U2.7 (A)
unnamed: R10.1, U1.12 (b)
unnamed: R10.2, U2.6 (B)
unnamed: R11.1, U1.11 (c)
unnamed: R11.2, U2.4 (C)
unnamed: R12.2, U1.3 (LT), U1.4 (BI), U1.5 (RBI)
unnamed: R13.1, U1.10 (d)
unnamed: R13.2, U2.2 (D)
unnamed: R14.1, U1.9 (e)
unnamed: R14.2, U2.1 (E)
unnamed: R15.1, U1.15 (f)
unnamed: R15.2, U2.9 (F)
unnamed: R16.1, U1.14 (g)
unnamed: R16.2, U2.10 (G)
unnamed: R19.1, SW3.1
unnamed: R21.1, SW4.1
VDD: J7.1, U3.1 (IP+), U3.2 (IP+)

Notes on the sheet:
myDAQ KONEKTOR
LEDice
5V LED INDIKATOR
*2k otpronici za crveni 7segm display
D5 to D12 = 2 A Fast diodes VF ≤ 1.2 V @ I = 2 A trr ≤ 200 ns 1N4007 SMD
5V i GND KONEKTORI
7SEGM + IC SN74LS47
POT
HALL SENZOR
POWER FLAGovi
L298N
MON. RUPE
TIPKALA
SKLOPKE
DODATNO NAPAJANJE I LED INDIKATOR
GND i AGND su spojeni jednim tanjim vodičem
LDR

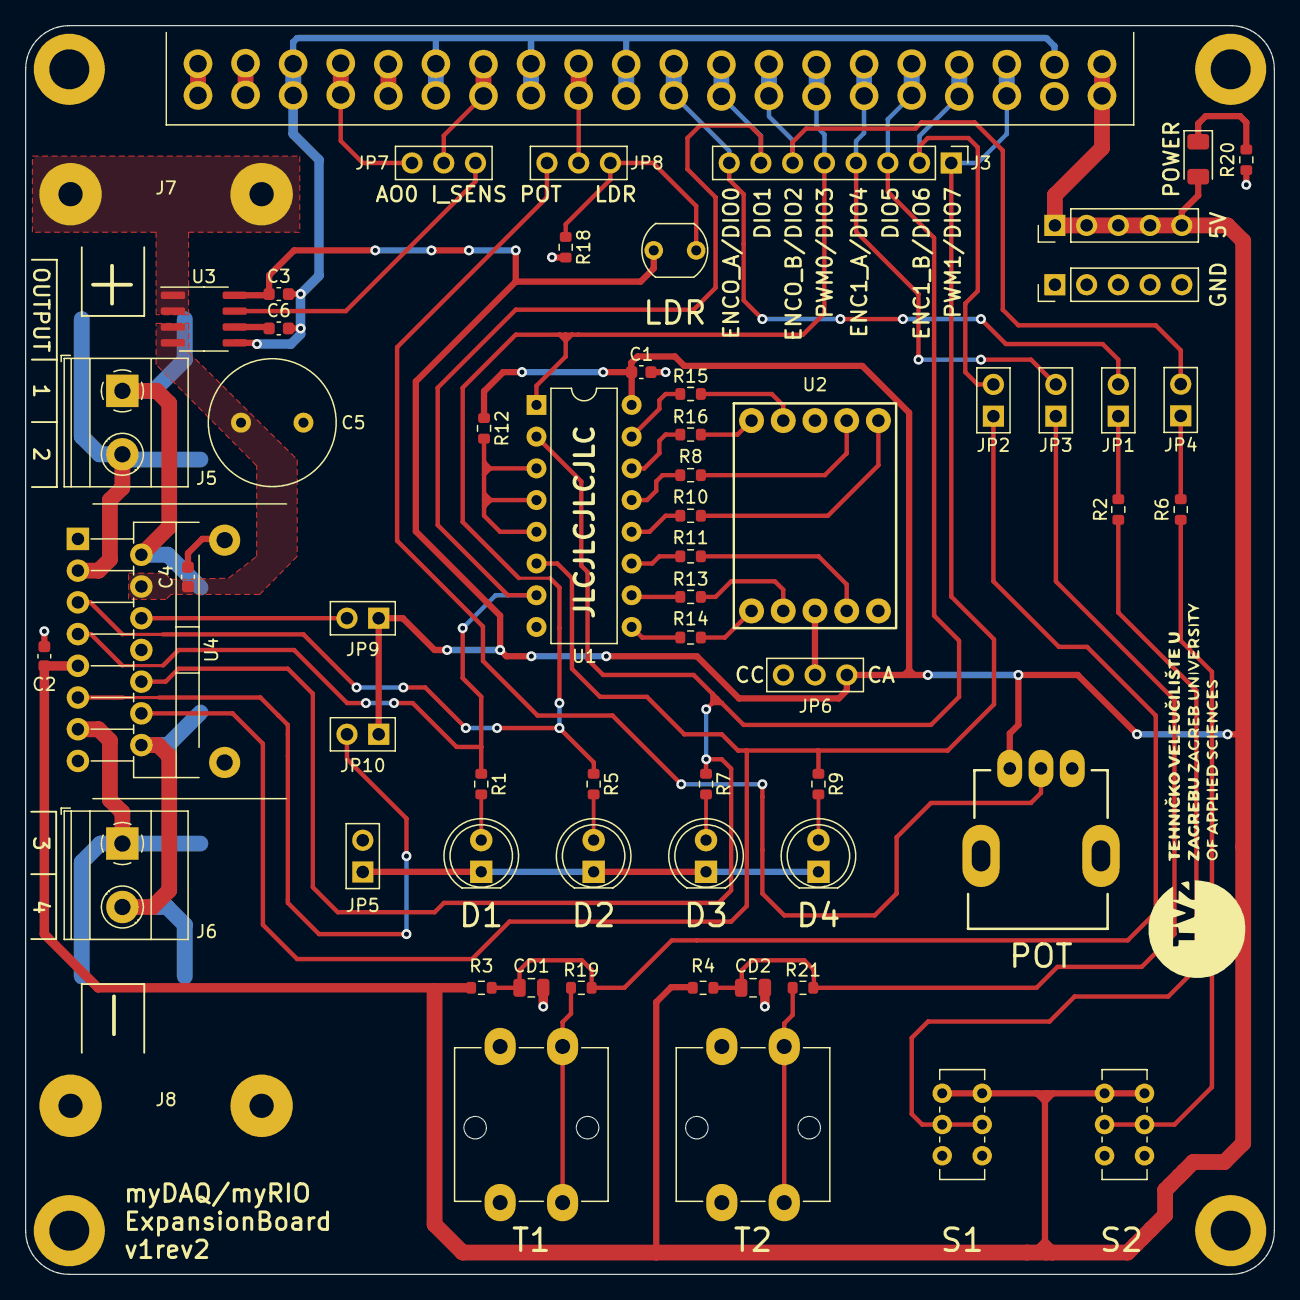
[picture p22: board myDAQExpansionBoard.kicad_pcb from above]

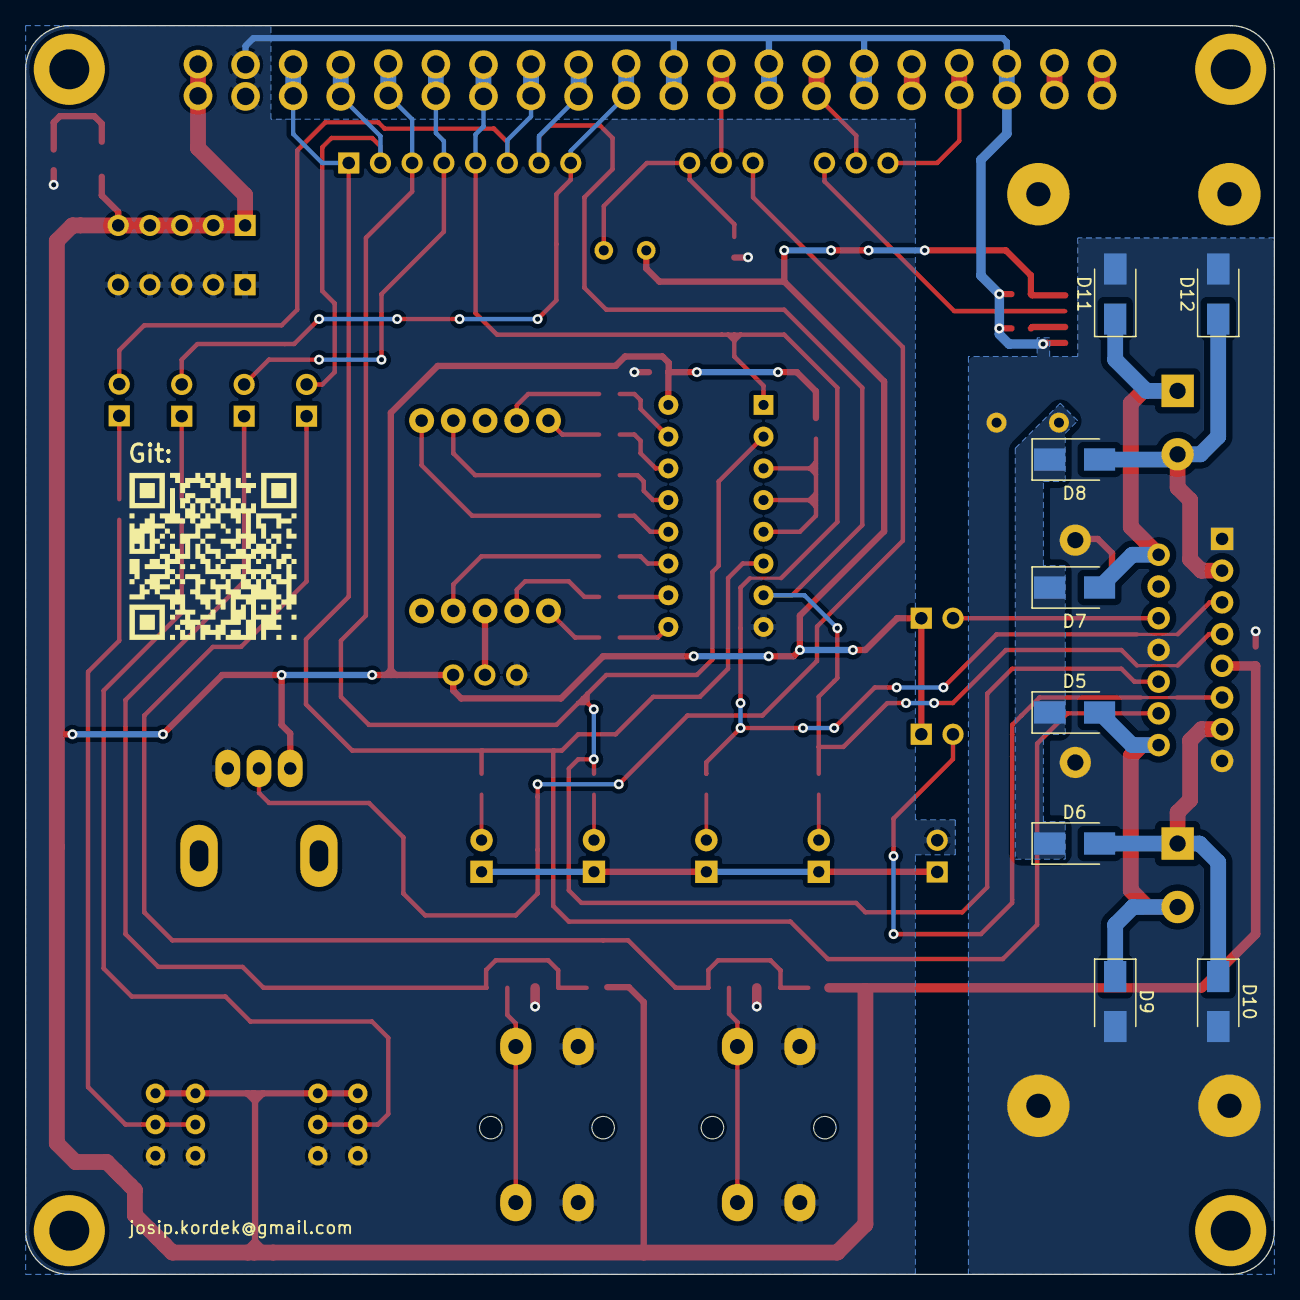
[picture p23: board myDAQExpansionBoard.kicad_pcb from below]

Board: 2 copper layers, 100.0 x 100.0 mm, 73 parts (8 on the bottom side), 55 nets.

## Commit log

2022-07-23 Initial release
    [myDAQExpansionBoard.kicad_pcb, myDAQExpansionBoard.kicad_sch]
2022-07-24 schematic first revision
    [myDAQExpansionBoard.kicad_sch]
2022-09-15 Inital release, board v1
2022-09-15 Initial release, board v1
    [BOM-myDAQExpansionBoard.csv, POS-myDAQExpansionBoard.csv, myDAQExpansionBoard-CuBottom.gbr, myDAQExpansionBoard-CuTop.gbr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]
2022-11-24 Added resistor for RC circuit
    [BOM-myDAQExpansionBoard.csv, POS-myDAQExpansionBoard.csv, myDAQExpansionBoard-B_Cu.gbr, myDAQExpansionBoard-B_Mask.gbr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]
